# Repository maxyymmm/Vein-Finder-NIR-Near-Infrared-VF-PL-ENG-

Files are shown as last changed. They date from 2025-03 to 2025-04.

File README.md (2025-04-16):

# ENG BELOW! <br> <br>
# 🔬 Skaner Żył NIR (Near-Infrared)  (VF)
### 📊 WYNIKI
#### Obraz zarejestrowany przez kamere NoIR
ori
#### CLAHE
CLAHE_samo
#### CLAHE + Median Filter
CLAHE MEDIAN

https://github.com/user-attachments/assets/bc7ac4bf-a98d-4c4a-9d43-718a29301329

https://github.com/user-attachments/assets/aef5d5cf-615a-48e7-bf75-2db40421cf0e

#### 📱 Widok w aplikacji
app10000
## 🎛️ Parametry sterowalne z aplikacji:
+ 🔁 **Liczba iteracji (for_value)** – Określa, ile razy poprawa kontrastu (CLAHE) jest stosowana. Więcej iteracji może zwiększyć widoczność żył, ale może też dodać szumy, a także znacznie spowolnić pracę urządzenia

+ 🌗 **Limit kontrastu (cliplimit_value)** – Kontroluje, jak mocno wzmacniany jest kontrast. Niższe wartości dają delikatniejsze efekty, wyższe mogą uwypuklić żyły, ale czasem pogarszają jakość obrazu.

+ 🔳 **Rozmiar siatki (tilegrid_value)** – Decyduje, na jak małe fragmenty dzielony jest obraz przy poprawie kontrastu. Większa siatka oznacza bardziej lokalne dostosowanie kontrastu.

+ 🔎 **Rozdzielczość (resolution)** – Ustawia rozdzielczość kamery.









### 🎯 Cel?
Celem tego projektu było stworzenie **przenośnego urządzenia do wizualizacji żył podskórnych w czasie rzeczywistym**, który będzie dostępny za znacznie niższą cenę niż obecnie dostępne profesjonalne urządzenia tego typu, których ceny zaczynają się od **3000$**. **Wykorzystano gotowe i łatwo dostępne do kupienia komponenty, aby zapewnić rozwiązanie jak najbardziej ekonomiczne i stosunkowo proste do samodzielnego złożenia.**
### ❓ Po co to wszystko?
Istnieją grupy chorych, dla których regularne przyjmowanie leków dożylnie (co 2/3 dni) stanowi konieczność, np. w przypadku chorób układu krzepnięcia. **Skaner żył jest narzędziem, które pomaga zminimalizować liczbę koniecznych wkłuć**, dzięki czemu można zmniejszyć niepotrzebny stres i ból dla pacjenta oraz zminimalizować liczbę prób, co jest szczególnie ważne w przypadku niemowląt i dzieci.
### ⚙️ Jak to działa?

new_scheme

🔬 **Skaner żył** to urządzenie, które wykorzystuje technologię **bliskiej podczerwieni _(NIR, ang. Near-InfraRed)_**, aby zobrazować żyły ukryte pod skórą pacjenta. 
Skaner żył działa w sposób następujący: urządzenie emituje bezpieczne dla organizmu fale podczerwone o długości fal w zakresie **700nm-1000nm _(w tym przypadku 850nm)_**, które przenikają przez skórę pacjenta. W momencie, gdy fale podczerwone trafiają na żyłę, zostają częściowo pochłonięte przez krew, a otaczające tkanki odbijają światło z powrotem. **_Zastosowanie kilku diod o różnych długościach fali może dać nieznacznie lepsze rezultaty, jednak nie ma gotowych układów pozwalających na taką funkcjonalność. Zbudowanie takiego skanera wymagałoby lutowania, stosowania oddzielnych źródeł napięcia i byłoby bardziej skomplikowane. Celem tego projektu było stworzenie stosunkowo prostego urządzenia, które spełnia swoje podstawowe funkcje w bezpieczny i skuteczny sposób._** <br>
W ten sposób kamera pozbawiona filtra **IR _(NoIR camera = No Infrared filter camera)_** rejestruje obraz, który następnie jest przetwarzany przez algorytm **CLAHE _(ang. Contrast Limited Adaptive Histogram Equalization)_** w celu podwyższenia kontrastu. 
Proces przetwarzania obejmuje następujące kroki: <br>
1️⃣ Konwersja obrazu do przestrzeni **barw LAB**.<br>
2️⃣ Zastosowanie **CLAHE** na kanale **L** **_(jasność)_**.<br>
3️⃣ Połączenie kanałów **LAB** z powrotem do obrazu **BGR**.<br>
4️⃣ Na obraz nakładany jest **filtr** **_(Median Filter)_**.<br>
Po przetworzeniu obrazu, jest on wysyłany na lokalny serwer **Flask** działający na urządzeniu. Aby zobaczyć strumień wideo ze skanera żył na innym urządzeniu, należy podłączyć się do hotspotu lokalnego Raspberry Pi. Następnie w przeglądarce internetowej wpisać **"veinfinder.local"** lub **"veinfinder.lan"** , ponieważ jest ustawiony **DNS**. Czasami jednak nie działa on w niektórych przeglądarkach – w takim przypadku należy wpisać adres IP Raspberry Pi: **"http://192.168.1.254/"** lub **"http://192.168.1.254:80"**
Urządzenie zostało wyposażone w baterię o pojemności **3000mah**, która pozwala na kilkanaście minut pracy.

### 🛠️ Sprzęt
💻 **Raspberry pi 4B 4GB**<br>
raspberry<br>
📸 **Kamera OdSeven Camera HD IR-CUT OV5647 5Mpx + moduły IR (850nm)** <br>
kamera<br>
🔋 **WaveShare Li-polymer Battery HAT** <br>
bateria<br>
💾 **Karta microSD** <br>
karta<br>
📦 **Obudowa** _(zaprojektowana w Fusion, należy wysłać pliki **.stl** do wydruku 3d)_ <br>

fusion
cura

### 💵 Koszty:
💻 Raspberry Pi 4B 4GB - **280 PLN** <br>
📸 Kamera OdSeven Camera HD IR-CUT OV5647 5Mpx + moduły IR (850nm) - **100 PLN** <br>
🔋 WaveShare Li-polymer Battery HAT - **90 PLN** <br>
💾 Karta microSD - **20 PLN** <br>
📦 Obudowa - Koszt wydruku ok **100 PLN** <br>
   **RAZEM ok 590 PLN**

### 📋 Wymagania
+ Raspberry Pi z zainstalowanym **Raspberry Pi OS (Legacy) 64-bit, 11 (bullseye), Kernel version: 6.1, Release date: October 22nd 2024**.

+ **Python** w wersji **3.9.2**.

### 🛠️ Konfiguracja Raspberry Pi
1️⃣ Pobranie plików z repozytorium na raspberry pi <br>
2️⃣ Instalacja potrzebnych bibliotek z pliku _**requirements.txt**_

Należy przejść do katalogu z pobranymi plikami i wpisać poniższą komendę: 
```console
veinfinder@veinfinder:~$ pip install -r requirements.txt
```

3️⃣ Utworzenie hotspotu **Wifi** + **DNS**
```console
veinfinder@veinfinder:~$ sudo apt update
veinfinder@veinfinder:~$ sudo apt install hostapd dnsmasq
```
upadte
```console
veinfinder@veinfinder:~$ sudo systemctl stop hostapd.service
veinfinder@veinfinder:~$ sudo systemctl stop dnsmasq.service
```
```console
veinfinder@veinfinder:~$ sudo nano /etc/dhcpcd.conf
```
nanoDhcpcd

Na końcu pliku należy dodać:
```console
interface wlan0
static ip_address=192.168.1.254/24
nohook wpa_supplicant
```
dhcpcfConf
```console
veinfinder@veinfinder:~$ sudo systemctl restart dhcpcd.service
```
```console
veinfinder@veinfinder:~$ sudo nano /etc/dnsmasq.conf
```
nanoDns

Na końcu pliku należy dodać:
```console
interface=wlan0
dhcp-range=192.168.1.10,192.168.4.50,255.255.255.0,24h
address=/veinfinder/192.168.1.254
```
dnsConf

```console
veinfinder@veinfinder:~$ sudo systemctl restart dnsmasq.service
```
```console
veinfinder@veinfinder:~$ sudo nano /etc/hostapd/hostapd.conf
```
hostapdConf

Należy wpisać w pliku:
```console
interface=wlan0
driver=nl80211
ssid=veinfinder
hw_mode=g
channel=7
wmm_enabled=0
macaddr_acl=0
auth_algs=1
ignore_broadcast_ssid=0
wpa=0
```
hostapdConf2

```console
veinfinder@veinfinder:~$ sudo nano /etc/default/hostapd
```
nanoHostapd
```console
DAEMON_CONF="/etc/hostapd/hostapd.conf"
```
Należy odnaleźć, odkomentować _**(usunąć znak "#")**_ i podać ścieżkę do pliku konfiguracyjnego. Powinno wyglądać to jak poniżej:
hostapdDeamon

```console
veinfinder@veinfinder:~$ sudo systemctl unmask hostapd
veinfinder@veinfinder:~$ sudo systemctl enable hostapd
veinfinder@veinfinder:~$ sudo systemctl start hostapd.service
```
Po wpisaniu:
```console
veinfinder@veinfinder:~$ sudo systemctl status hostapd
```
Powinna wyświetlić się podobna odpowiedź ze statusem **"active"**
hostapdStatus2

4️⃣ Ustawienie automatycznego włączania programu przy starcie urządzenia _**app.py**_
```console
veinfinder@veinfinder:~$ sudo nano /etc/rc.local
```
rclocal1

Należy dopisać na końcu, ale **przed** "exit 0": 
```console
sudo python3 SCIEŻKA_PLIKU/app.py &
```
W tym przypadku:
```console
sudo python3 /home/veinfinder/Desktop/Veinfinder/app.py &
```
rclocal2

5️⃣ Dla uzyskania lepszej wydajności można wyłączyć bluetooth oraz włączyć tryb konsolowy

*Wyłączenie bluetooth*
```console
sudo nano /boot/config.txt
```
turnOffBluetooth

Należy wpisać na końcu pliku:
```console
dtoverlay=disable-bt
```
turnOffBluetooth2

*Włączenie trybu konsolowego* 
```console
sudo raspi-config
```
raspiconfig1

_*"System Options -> Boot / Auto Login Select boot... -> Console Autologin..."*_
raspiconfig2
raspiconfig3
raspiconfig4

✅ **GOTOWE!**

### ▶️ Użytkowanie
Urządzenie włączamy przyciskiem **ON/OFF** <br>
Urządzenie wyłączamy naciskając dwukrotnie przycisk **ON/OFF** <br>
Urządzenie można ładować za pomocą **USB TYP C (wspierane szybkie ładowanie)** (5 diod LED wskazuje poziomu naładowania baterii oraz statusu ładowania) <br> <br>

# ENG
# 🔬 Vein Finder NIR (Near-Infrared) (VF)
### 📊 RESULTS
#### Image captured by NoIR camera
ori
#### CLAHE
CLAHE_samo
#### CLAHE + Median Filter
CLAHE MEDIAN

https://github.com/user-attachments/assets/bc7ac4bf-a98d-4c4a-9d43-718a29301329

https://github.com/user-attachments/assets/aef5d5cf-615a-48e7-bf75-2db40421cf0e

#### 📱 View in the Application
app10000
## 🎛️ Parameters Adjustable from the Application:
+ 🔁 **Number of Iterations (for_value)** – Controls how many times the CLAHE contrast enhancement process is repeated. More iterations may improve vein visibility but can also add noise and significantly slow down the device.

+ 🌗 **Contrast Limit (cliplimit_value)** – Controls how strongly the contrast is enhanced. Lower values result in a more subtle contrast enhancement, while higher values can make veins more visible but may also degrade image quality

+ 🔳 **Grid Size (tilegrid_value)** – Defines how small the image is divided into sections for contrast enhancement. A larger grid means more localized contrast adjustments.

+ 🔎 **Resolution (resolution)** – Sets the camera resolution.









### 🎯 Purpose?
The aim of this project was to create a **portable device for visualizing subcutaneous veins in real-time**, which would be available at a much lower cost than currently available professional devices of this type, which start at **$3000**. **Ready-made and easily accessible components were used to provide the most economical and relatively simple solution for self-assembly.**
### ❓ Why all this?
There are groups of patients for whom regular intravenous drug administration (every 2/3 days) is necessary, e.g., in the case of coagulation system disorders. **Vein finder is a tool that helps minimize the number of necessary punctures**, thus reducing unnecessary stress and pain for the patient and minimizing the number of attempts, which is particularly important for infants and children.
### ⚙️ How does it work?
new_scheme

🔬 **Vein scanner** is a device that uses **near-infrared technology (NIR)** to visualize veins hidden under the patient's skin. The vein scanner works as follows: the device emits safe infrared waves with wavelengths in the range of **700nm-1000nm _(in this case 850nm)_**, which penetrate the patient's skin. When the infrared waves hit the vein, they are partially absorbed by the blood, and the surrounding tissues reflect the light back. **_The use of several diodes with different wavelengths may give slightly better results, but there are no ready-made circuits that allow for such functionality. Building such a scanner would require soldering, separate voltage sources, and would be more complicated than what has been achieved in this project. The goal of this project was to create a relatively simple device that fulfills its basic functions in a safe and effective way._** <br>
The camera that is devoid of an **IR filter _(NoIR camera = No Infrared filter camera)_**, records the image, which is then processed by the **CLAHE algorithm _(Contrast Limited Adaptive Histogram Equalization)_** to enhance the contrast.
The processing process involves the following steps: <br>
1️⃣ Conversion of the image to the **LAB color space**.<br>
2️⃣ Applying **CLAHE** to the **L channel _(Lightness)_**.<br>
3️⃣ Merging the **LAB channels** back to the **BGR** image.<br>
4️⃣ A **filter (Median Filter)** is applied to the image.<br>
After processing the image, it is sent to a local **Flask** server running on the device.  
To view the video stream from the vein scanner on another device, connect to the Raspberry Pi's local hotspot.  
Then, open a web browser and enter **"veinfinder.local"** or **"veinfinder.lan"** as the **DNS** is set up.  
However, it may not work in some browsers – in that case, enter the Raspberry Pi's IP address: **"http://192.168.1.254/"** or **"http://192.168.1.254:80"**  

The device is equipped with a **3000mAh** battery, allowing for several minutes of operation.
### 🛠️ Hardware
💻 **Raspberry Pi 4B 4GB**<br>
raspberry<br>
📸 **OdSeven Camera HD IR-CUT OV5647 5Mpx + IR modules (850nm)** <br>
kamera<br>
🔋 **WaveShare Li-polymer Battery HAT** <br>
bateria<br>
💾 **MicroSD Card** <br>
karta<br>
📦 **Case** _(designed in Fusion, **.stl** files need to be sent for 3d printing)_ <br>
fusion
cura

### 💵 Costs:
💻 Raspberry pi 4B 4GB - **280zł** <br>
📸 OdSeven Camera HD IR-CUT OV5647 5Mpx + moduły IR (850nm) - **100zł** <br>
🔋 WaveShare Li-polymer Battery HAT - **90zł** <br>
💾 microSD Card- **20zł** <br>
📦 Case - 3d printing cost approximately **100zł** <br>
**TOTAL** approximately **590 PLN** ~ **155 USD**

### 📋 Requirements
+ Raspberry Pi with **Raspberry Pi OS (Legacy) 64-bit, 11 (Bullseye), Kernel version: 6.1, Release date: October 22nd, 2024**.

+ **Python** version **3.9.2**.

### 🛠️ Raspberry Pi Configuration
1️⃣ Downloading files from the repository to Raspberry Pi  
2️⃣ Installing required libraries from the _**requirements.txt**_ file

You need to navigate to the directory with the downloaded files and enter the following command:
```console
veinfinder@veinfinder:~$ pip install -r requirements.txt
```

3️⃣ Creating a **Wifi Hotspot** + **DNS**
```console
veinfinder@veinfinder:~$ sudo apt update
veinfinder@veinfinder:~$ sudo apt install hostapd dnsmasq
```
upadte
```console
veinfinder@veinfinder:~$ sudo systemctl stop hostapd.service
veinfinder@veinfinder:~$ sudo systemctl stop dnsmasq.service
```
```console
veinfinder@veinfinder:~$ sudo nano /etc/dhcpcd.conf
```
nanoDhcpcd

At the end of the file, add:
```console
interface wlan0
static ip_address=192.168.1.254/24
nohook wpa_supplicant
```
dhcpcfConf
```console
veinfinder@veinfinder:~$ sudo systemctl restart dhcpcd.service
```
```console
veinfinder@veinfinder:~$ sudo nano /etc/dnsmasq.conf
```
nanoDns

At the end of the file, add:
```console
interface=wlan0
dhcp-range=192.168.1.10,192.168.4.50,255.255.255.0,24h
address=/veinfinder/192.168.1.254
```
dnsConf

```console
veinfinder@veinfinder:~$ sudo systemctl restart dnsmasq.service
```
```console
veinfinder@veinfinder:~$ sudo nano /etc/hostapd/hostapd.conf
```
hostapdConf

Enter the following in the file:
```console
interface=wlan0
driver=nl80211
ssid=veinfinder
hw_mode=g
channel=7
wmm_enabled=0
macaddr_acl=0
auth_algs=1
ignore_broadcast_ssid=0
wpa=0
```
hostapdConf2

```console
veinfinder@veinfinder:~$ sudo nano /etc/default/hostapd
```
nanoHostapd
```console
DAEMON_CONF="/etc/hostapd/hostapd.conf"
```
You need to find, uncomment **(remove the "#" character)**, and provide the path to the configuration file. It should look like this:  
hostapdDeamon

```console
veinfinder@veinfinder:~$ sudo systemctl unmask hostapd
veinfinder@veinfinder:~$ sudo systemctl enable hostapd
veinfinder@veinfinder:~$ sudo systemctl start hostapd.service
```
After running the command:
```console
veinfinder@veinfinder:~$ sudo systemctl status hostapd
```
A similar response should appear with the status **"active"**
hostapdStatus2

4️⃣ Setting up automatic startup for _**app.py**_ at device boot
```console
veinfinder@veinfinder:~$ sudo nano /etc/rc.local
```
rclocal1

It should be added at the end, but **before** "exit 0": 
```console
sudo python3 FILE_PATH/app.py &
```
In this case:
```console
sudo python3 /home/veinfinder/Desktop/Veinfinder/app.py &
```
rclocal2

5️⃣ For better performance, you can disable Bluetooth and enable console mode

*Disabling Bluetooth*
```console
sudo nano /boot/config.txt
```
turnOffBluetooth

At the end of the file, add:
```console
dtoverlay=disable-bt
```
turnOffBluetooth2

*Enabling Console Mode* 
```console
sudo raspi-config
```
raspiconfig1

_*"System Options -> Boot / Auto Login Select boot... -> Console Autologin..."*_
raspiconfig2
raspiconfig3
raspiconfig4

✅ **READY!**

### ▶️ Usage
To turn on the device, press the **ON/OFF** button. <br>
To turn off the device, press the **ON/OFF** button twice. <br>
The device can be charged using USB TYPE C (Fast charging supported).  _(The five LED indicators show the battery level and charging status)_

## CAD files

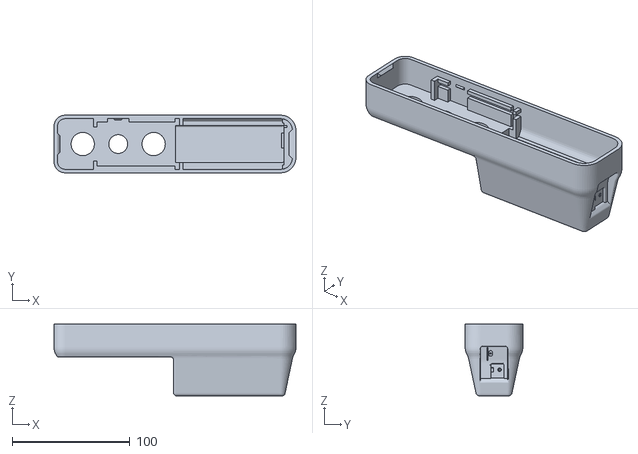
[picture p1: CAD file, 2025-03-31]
Case/MainCase.stl
205.6 x 49.0 x 61.1

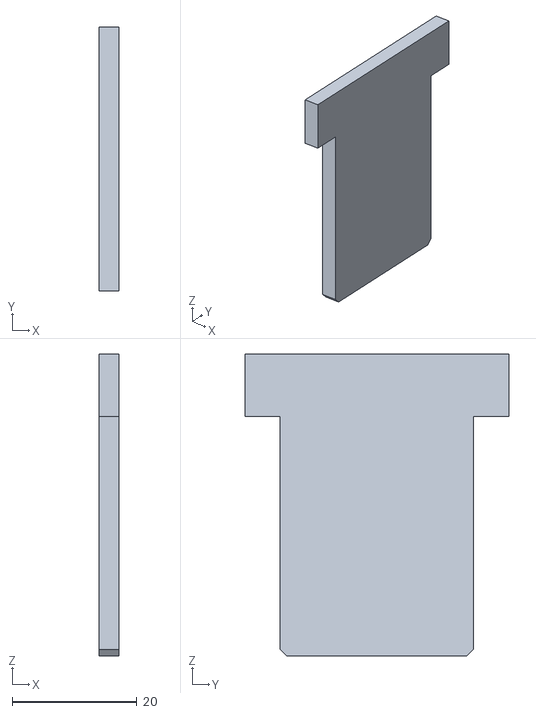
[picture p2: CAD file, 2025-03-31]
Case/RaspberryHoldingPlate.stl
3.20 x 42.4 x 48.5

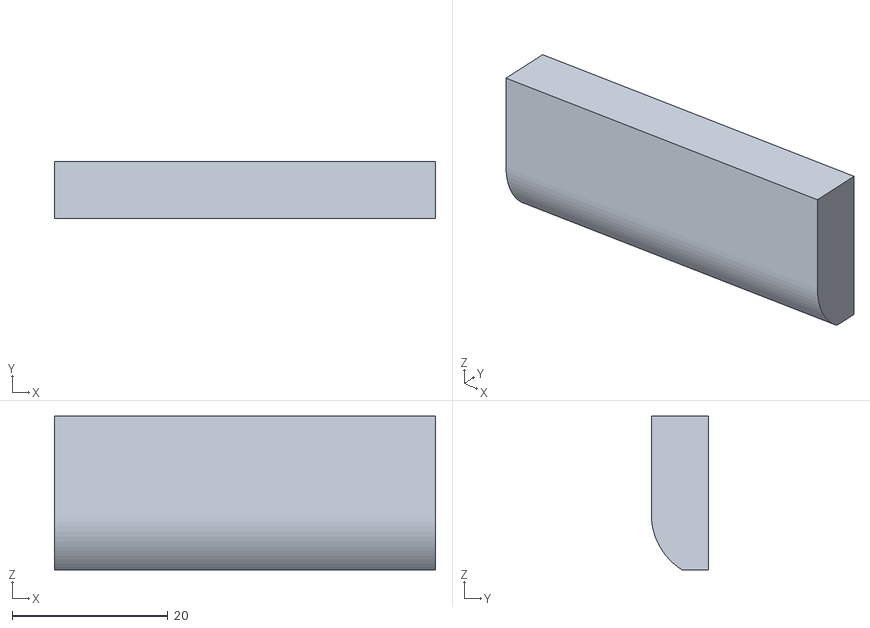
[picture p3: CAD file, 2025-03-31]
Case/BatteryHoldingPlate.stl
49.0 x 7.38 x 19.8

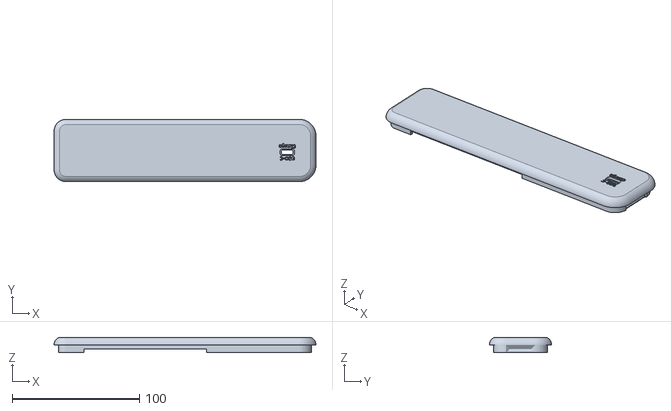
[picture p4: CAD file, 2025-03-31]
Case/Lid.stl
205.6 x 49.0 x 12.0

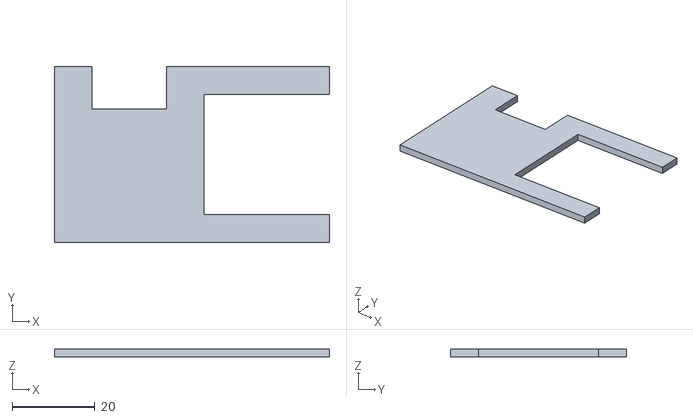
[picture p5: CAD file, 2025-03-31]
Case/CameraHoldingPlate.stl
66.3 x 42.4 x 2.00

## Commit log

2025-02-25 Cleaned up commit history for improved repository structure
    [Case_stl.stl]
2025-02-25 Refactored CLAHE parameter handling and added frontend controls
    - Implemented dynamic CLAHE parameter updates via frontend UI
    - Improved camera resolution selection and initialization
    - Added parameter saving/loading functionality
    - Updated README with new setup instructions
    - Enhanced error handling and logging in `ParamSetter.py`
2025-03-07 Enhance Logging, UI Display, and Default Settings + Update 3D Case Files
    In app.py:
    -Added real-time logging and improved comments for
    better clarity.
    In default_config.json:
    -Updated default resolution to 1280x720
    In index.html:
    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
    [BatteryHoldingPlate.stl, CameraHoldingPlate.stl, Case_stl.stl, Lid.stl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]
